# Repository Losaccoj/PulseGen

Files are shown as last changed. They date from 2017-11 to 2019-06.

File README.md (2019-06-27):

# PulseGen
Teensy-driven pulse generator for TTL pulse trains (e.g. for optogenetic experiments).
The enclosure STL files are in the folder entitled 'Enclosure'. There is also a bill of materials and rough wiring guide. 

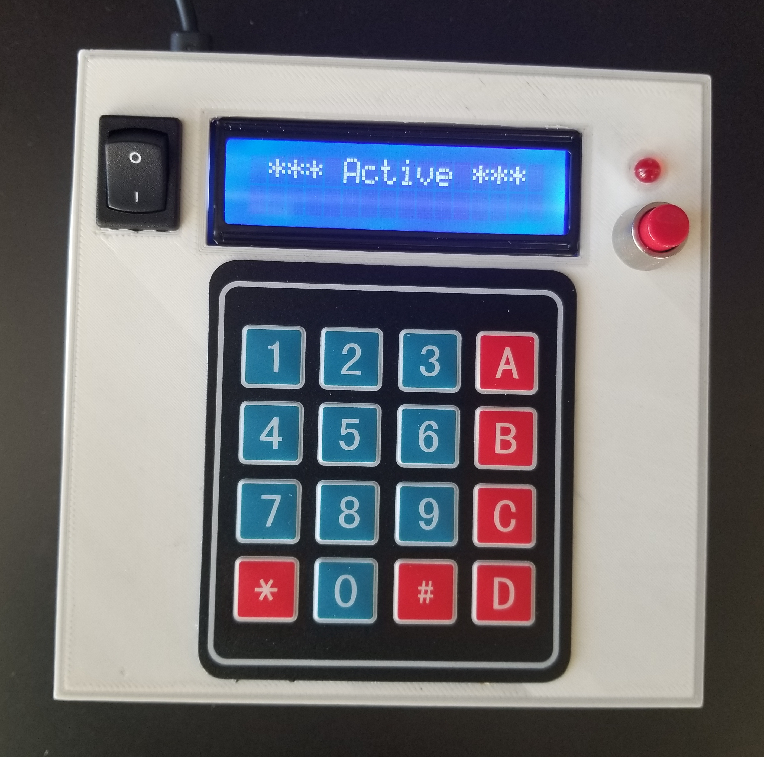
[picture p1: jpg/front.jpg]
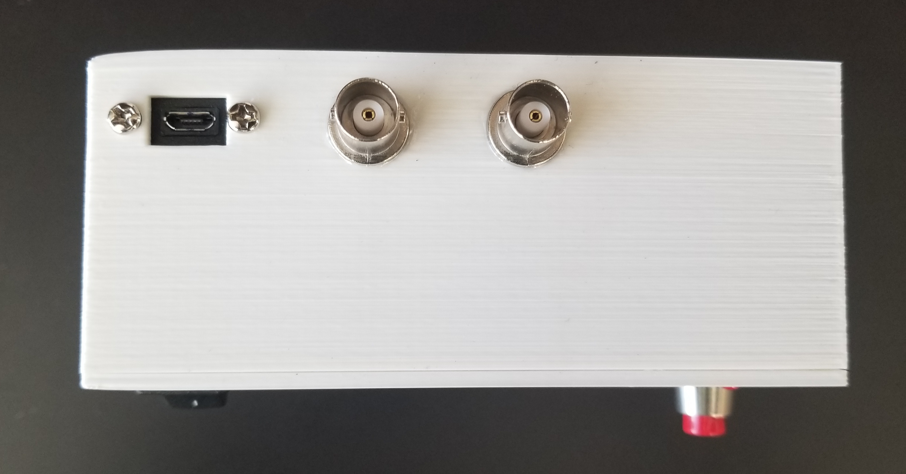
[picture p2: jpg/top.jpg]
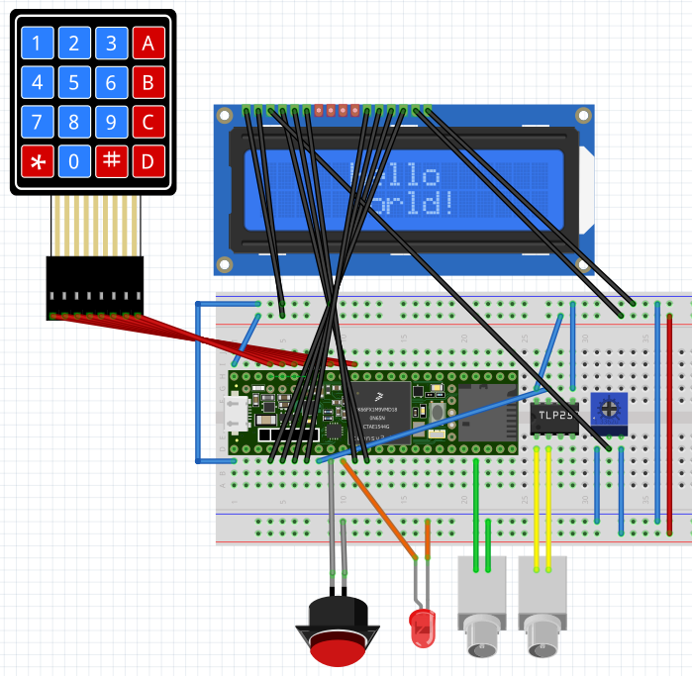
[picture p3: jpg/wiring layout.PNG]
  

## Pulse Timing
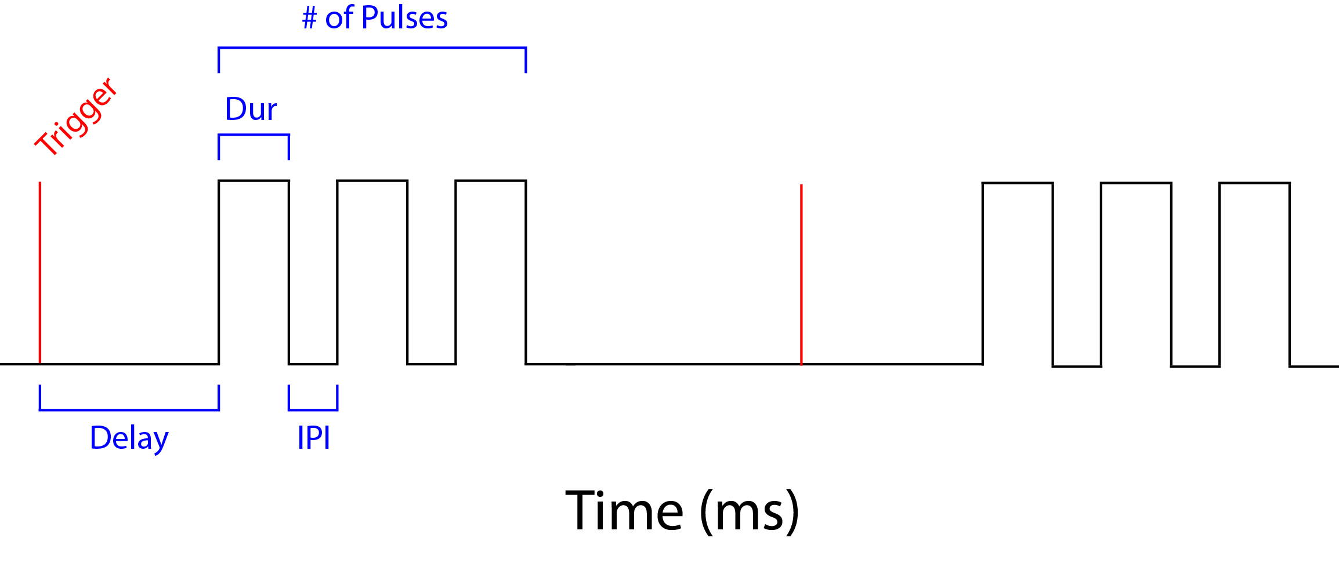
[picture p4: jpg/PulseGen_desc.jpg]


> - Trigger: External 5V TTL input to initiate stimulation OR button-press on PulseGen
> - Delay: Time delay between trigger and stimulus. Set to 0 for immediate stimuluation with trigger
> - Dur: Duration/pulse width
> - IPI: Inter-pulse interval
> - \# of Pulses: Number of pulses in "pulse train". Set to 1 for one pulse

### Usage
1. Upon boot (after splash screen (splash)), user must input stimulus parameters (user_params) on keypad following prompts. 
   - #: Enter     
   - *: Clear 
  
2. Once stimulus parameters are established, PulseGen waits for an input before sending triggers out (stim_gen) according to the stimulus parameters. These triggers can either be:
   - Manual button-press (trig2)
   - TTL input (trig1)

   In either input case, stimulus triggers are sent out over TTL1 (e.g. BNC cable) and LED1 (on face of device) simultaneously according to the stimulus parameters. 

#### Acknowledgments
My initial source of inspiration came from Andrew Scallon at the Optogenetics and Neural Engineering <a href="https://optogeneticsandneuralengineeringcore.github.io/ONECoreSite/">(ONE) Core</a> at the University of Colorado, Anschutz Medical Center. 

I would also like to thank the folks behind <a href="https://sanworks.io/shop/viewproduct?productID=1102">Pulse Pal</a> (Joshua Sanders (the founder) as well as contributers Josh Siegle and Goncalo Lopes) for inspiration as to the feasibility of the project as well as the idea for the opto-isolation (TLP2530) protection of the Teensy. 

The characterization of the Pulse Pal's performance in this paper by <a href="https://www.ncbi.nlm.nih.gov/pmc/articles/PMC4263096/">Sanders and Kepecs 2014</a> is admirable and I intend to do the same with PulseGen as well.

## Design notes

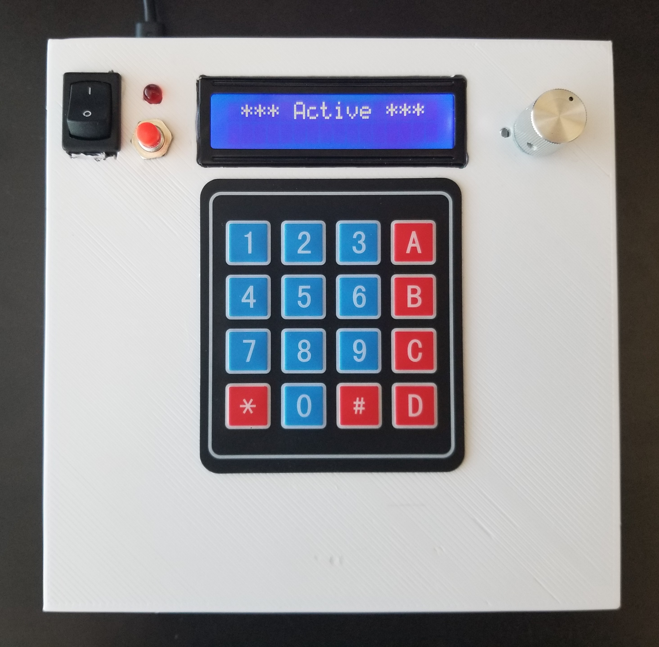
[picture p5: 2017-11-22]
jpg/PulseGen_face.jpg

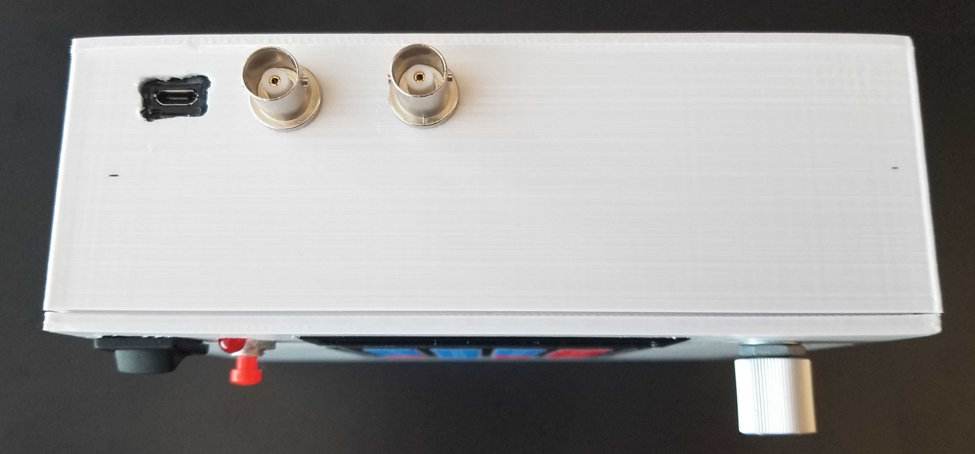
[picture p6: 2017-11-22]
jpg/PulseGen_connections.jpg

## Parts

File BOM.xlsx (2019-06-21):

Part Name | Quantity | Link | Distributor | Catalog Number | Generic Part Number
Teensy 3.5 | 1 | https://www.pjrc.com/store/teensy35.html | PJRC | N/A | N/A
LCD Panel | 1 | https://www.adafruit.com/product/181 | Adafruit | 181 | 1602A
Keypad | 1 | https://www.adafruit.com/product/419 | Adafruit | 419 | ZRX-543
Micro-USB Panel Mount | 1 | https://www.adafruit.com/product/3258 | Adafruit | 3258 | N/A
SPST Switch | 1 | https://www.digikey.com/product-detail/en/cw-industries/GRS-4011-0076/SW323-ND/161452 | Digikey | SW323-ND | N/A
Optoisolator | 1 | https://www.digikey.com/product-detail/en/toshiba-semiconductor-and-storage/TLP2530-F/TLP2530F-ND/871253 | Digikey | TLP2530F-ND | TLP2530
BNC Panel Mount | 2 | https://www.digikey.com/product-detail/en/amphenol-rf-division/31-221-RFX/ARFX1064-ND/100648 | Digikey | ARFX1064-ND | N/A
5mm diameter LED | 1 | https://www.digikey.com/products/en?keywords=160-1128-ND%20 | Digikey | 160-1128-ND | N/A
Push button | 1 | https://www.digikey.com/product-detail/en/e-switch/PS1024ARED/EG2015-ND/44577 | Digikey | EG2015-ND | N/A
Case bottom | 1 | https://github.com/Losaccoj/PulseGen/tree/master/Enclosure | N/A | N/A | N/A
Case lid | 1 | https://github.com/Losaccoj/PulseGen/tree/master/Enclosure | N/A | N/A | N/A

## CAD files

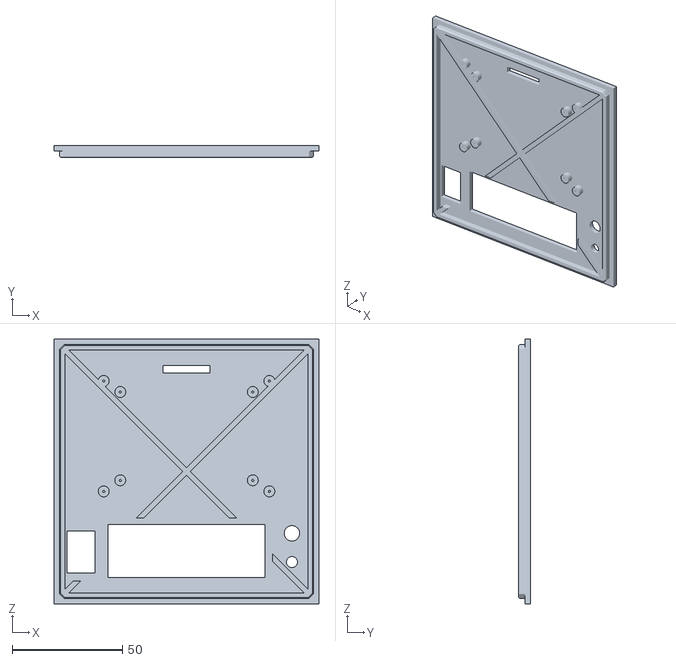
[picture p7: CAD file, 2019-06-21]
Enclosure/Lid.stl
120.0 x 5.50 x 120.0

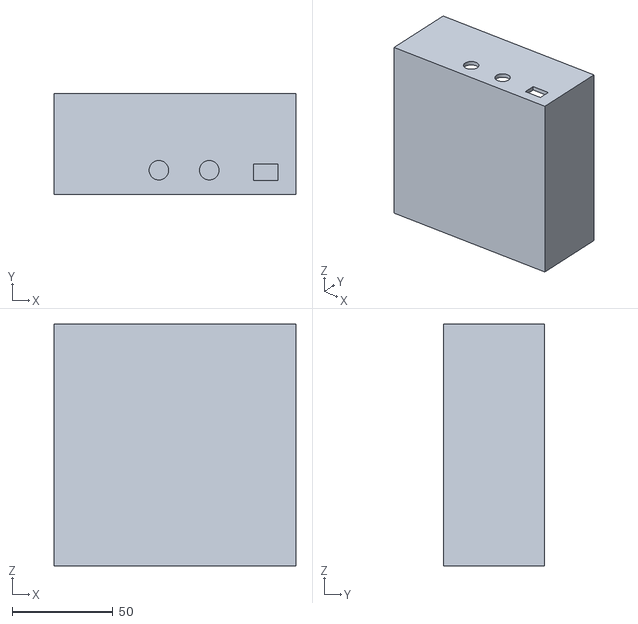
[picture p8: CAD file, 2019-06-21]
Enclosure/Case.stl
120.0 x 50.0 x 120.0

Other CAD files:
Enclosure/Case.f3d
Enclosure/Lid.f3d

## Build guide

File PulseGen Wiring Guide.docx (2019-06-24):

PulseGen Wiring Guide

Make breadboard power supply rails for 3.3V, 5V, and GND from Teensy.

Teensy pins are referred to as T + pin number (e.g. T6)

TLP2530 (Optocoupler)

1: Trig in signal (BNC in)

2: Trig in GND

5: PSU GND

7: Out 1 (trig 1, T6)

8: Vcc (5V)

Button (trigger)

T7 (trig2 button)

GND

Output

T29 (TTL1 BNC out)

T8 (LED1)

LCD 1602A

1: GND

2: 5V

3: Middle of trimmer pot

4: RS (T10)

5: GND

6: EN (T9)

11: T5

12: T4

13: T3

14: T2

15: 5V

16: GND

Trimmer pot (for LCD contrast. Mount to board, adjust during first usage)

L: GND

M: 1602A #3

R: 5V

Keypad ZRX-543

T16: Zrx 1 Zrx 1-4 are rows T20-23 are rows

… Zrx 5-8 are cols T16-19 are cols

T23: Zrx 8

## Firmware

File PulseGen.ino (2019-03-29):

/* PulseGen 2017
Written by Justin Losacco
MIT-licensed, freely available on GitHub */

// include the library code:
#include <LiquidCrystal.h>
#include <Bounce.h>
#include <Key.h>
#include <Keypad.h>

//Keypad initialization stuff
const byte ROWS = 4; //four rows
const byte COLS = 4; //four columns
char keys[ROWS][COLS] = {
  {'1', '2', '3', 'A'},
  {'4', '5', '6', 'B'},
  {'7', '8', '9', 'C'},
  {'*', '0', '#', 'D'}
};

byte rowPins[ROWS] = {23, 22, 21, 20}; //connect to the row pinouts of the keypad
byte colPins[COLS] = {19, 18, 17, 16}; //connect to the column pinouts of the keypad
Keypad keypad = Keypad( makeKeymap(keys), rowPins, colPins, ROWS, COLS );

// initialize library by pairinig LCD pin w/ Teensy pin
const int rs = 10, en = 9, d4 = 5, d5 = 4, d6 = 3, d7 = 2;
LiquidCrystal lcd(rs, en, d4, d5, d6, d7);

// Define stim-associated pins on Teensy:
const int trig1 = 6; //input trigger from behavioral PC. (AKA in_trig)
const int trig2 = 7; //button on PulseGen
const int TTL1 = 29; //output TTL trigger to laser
const int LED1 = 8; //output LED on PulseGen
Bounce in_trig1 = Bounce(trig1, 10);     //Debounce
Bounce in_trig2 = Bounce(trig2, 10);     //Debounce

const char* char_params[] = {"Delay (ms)", "Duration (ms)", "IPI (ms)", "# of Pulses"};
int int_params[] = {' ', ' ', ' ', ' ', ' '}; //Allow for 4 entries pertaining to the char params strings.

//Define stim params
String temp_input; //Bad for ucontrollers bc fragments memory
char tot_str;
const char stored[8] = "Stored ";    
char whichKey;

void setup() {
  lcd.begin(16, 2);
  Serial.begin(9600);
  pinMode(TTL1, OUTPUT);
  pinMode(LED1, OUTPUT);
  pinMode(trig1, INPUT_PULLUP);      //use pull-up resistor to set default to high
  pinMode(trig2, INPUT_PULLUP);      //use pull-up resistor to set default to high
  keypad.setDebounceTime(50);        //Debounce keypad
  splash();                          //Splash (welcome) screen
  delay(250);
  user_params();                     //Parameter setup
  delay(5);
}

void loop() {
  stim_gen();
}

void splash() {
  //Print splash screen to LCD
  lcd.setCursor(0, 0);
  lcd.print("Pulse Generator");
  lcd.setCursor(0, 1);
  lcd.print("     2017");
  delay (1500);
  lcd.clear();
}

void user_params() {
  static int numpos = 0;
  static int itNo = 0;  
  while (itNo < 4) {                             //Iterate through each of 4 stim params
    lcd.setCursor(0, 0);
    lcd.print(char_params[itNo]);
    char whichKey = keypad.waitForKey();         //Previously char whichKey = keypad.getKey();
    if (whichKey == 'B' || whichKey == 'D' ) {   //define invalid keys
      lcd.clear();
      lcd.setCursor(0, 0);
      lcd.print("  Invalid Key!");
      delay(1000);
      lcd.clear();
    }
    if (isDigit(whichKey)) {
      temp_input += whichKey;
      lcd.setCursor(0, 1);
      lcd.print("                                ");
      lcd.setCursor(0, 1);
      lcd.print(temp_input);
      numpos ++;
    }
    if (whichKey == '#') {          // # = Enter
      int_params[itNo] = temp_input.toInt();
      lcd.clear();
      lcd.setCursor(0, 1);
      lcd.print(stored + temp_input);
      delay(2500);           
      temp_input.remove(0);         //clear temp_input since it's been transferred to int_params;
      lcd.setCursor(0, 1);            //Clear line 2
      lcd.print("                                ");
      itNo++;
    }
    if (whichKey == '*') {   // * = Erase value
      lcd.clear();
      lcd.setCursor(0, 1);
      lcd.print("    Erased");
      temp_input.remove(0);
      delay(1000);
      lcd.setCursor(0, 1);            //Clear line 2
      lcd.print("                                ");
  }
  }

lcd.clear();
lcd.setCursor(0, 0);
lcd.print(" *** Active ***");
}

void stim_gen() {
  if (in_trig1.update() || in_trig2.update()) {              //look @ trig1 to see if changed state
    if (in_trig1.fallingEdge() || in_trig2.fallingEdge()) {        //and it was a falling edge
      for (int count = 0; count < int_params[3]; count++)  {  //Create new var count to act as place-holder/counter
        delay(int_params[0]);
        digitalWrite(TTL1, HIGH);
        digitalWrite(LED1, HIGH);
        delay(int_params[1]);
        digitalWrite(TTL1, LOW);
        digitalWrite(LED1, LOW);
        delay(int_params[2]);
      }
    }
  }
}

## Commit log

2018-04-06 Added part files for enclosure
    [pulsegen_bottom.SLDPRT, pulsegen_bottom.STL, pulsegen_top.SLDPRT, pulsegen_top.STL]
2018-04-06 Added enclosure part files
2019-06-21 update readme.md
    Indicated location of enclosure STL files
2019-06-21 Added new enclosure design
    [Case.stl, Lid.stl]
2019-06-21 Added BOM
    [BOM.xlsx]
2019-06-21 Added rough wiring guide
    I'm hoping to improve this in the future. But this should get you going!
2019-06-24 Added Teensy 3.5 pinout from PJRC.com
2019-06-24 Added rough wiring guide
2019-06-27 PulseGen breadboard Fritzing diagram
    In case it's useful to have this file for laying out the connections, here you go!
    [PulseGen.fzz]
2019-06-27 Added wiring schematic
